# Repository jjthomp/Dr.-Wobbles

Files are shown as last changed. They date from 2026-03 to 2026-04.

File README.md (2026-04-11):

# Dr. Wobbles – Low-Cost Open Source Pain Relief Device

Dr. Wobbles is a compact, wearable medical device designed to reduce procedural pain during injections through combined vibration and cooling. It was developed by UBC SBME Capstone Team 12 in partnership with the Digital Lab (September 2025 – April 2026), with a primary focus on children living with Juvenile Idiopathic Arthritis (JIA) and broader applicability across injection-based clinical settings.

---

## Repository Contents

### 📁 `/PCB`
Contains all files required for PCB fabrication and assembly.
- Gerber files (for PCB manufacturer submission)
- Drill files
- Bill of Materials (BOM)
- Fusion Electronics source files
- PCB schematic and routing diagrams

> For assembly instructions, see the [Assembly Guide](#assembly--instructions-for-use) section below.

---

### 📁 `/CAD`
Contains all 3D model files for the mechanical housing, designed in OnShape.
- `housing_bottom.stl` – Bottom housing piece with battery and motor slots
- `housing_lid.stl` – Top lid piece with twist-and-lock mechanism and strap tabs
- `pcb_holder.stl` – Circuit board housing insert (for use with custom PCB)
- `breadboard_holder.stl` – Circuit board housing insert (for use with breadboard prototype)
- OnShape source files

> All parts are designed to be 3D printed.

---

### 📁 `/Software`
Contains the firmware for the Adafruit QTPY ESP32-S2 microcontroller.
- `dr_wobbles.ino` – Main Arduino firmware file

**Key firmware features:**
- Two vibration intensities: LOW (PWM 120/255) and HIGH (PWM 255/255)
- 5-minute auto-shutoff on HIGH setting
- Light-sleep mode during OFF state to conserve battery
- Debounce logic for button inputs

To set up the Arduino environment for the QTPY ESP32-S2, follow the official Adafruit guide:  
👉 https://learn.adafruit.com/adafruit-qt-py-esp32-s3/arduino-ide-setup-4mb-2mb-psram

### 📁 `/Docs`
Contains the complete bill of materials and sticker design
- Sticker design
- Bill of materials

> For assembly instructions, see the [Assembly Guide](#assembly--instructions-for-use) section below.
---

## Assembly & Instructions for Use

Full step-by-step assembly and usage guides are available online:

- **Assembly Manual:** https://jjthomp.github.io/Dr.-Wobbles/
- **Instructions for Use:** https://jjthomp.github.io/Dr.-Wobbles/

---

## License
This project is open source. All hardware, software, and documentation are freely available for use, modification, and distribution. Please credit UBC SBME Capstone Team 12 and the Digital Lab if you build upon this work.

---

## Contact
For questions about this project, please contact the Digital Lab or open an issue in this repository.

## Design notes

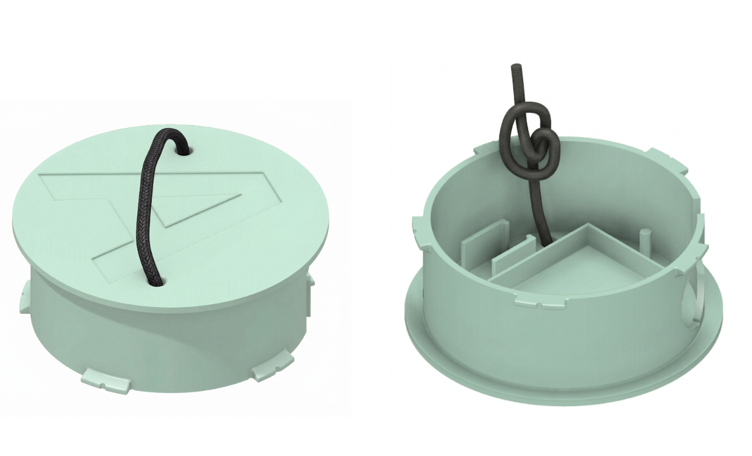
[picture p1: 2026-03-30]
images/elasticband.png

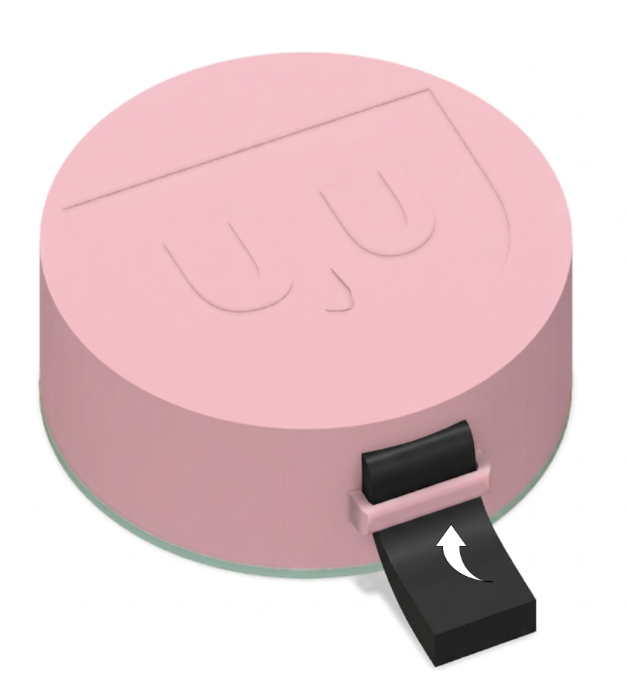
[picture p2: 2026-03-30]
images/strap.png

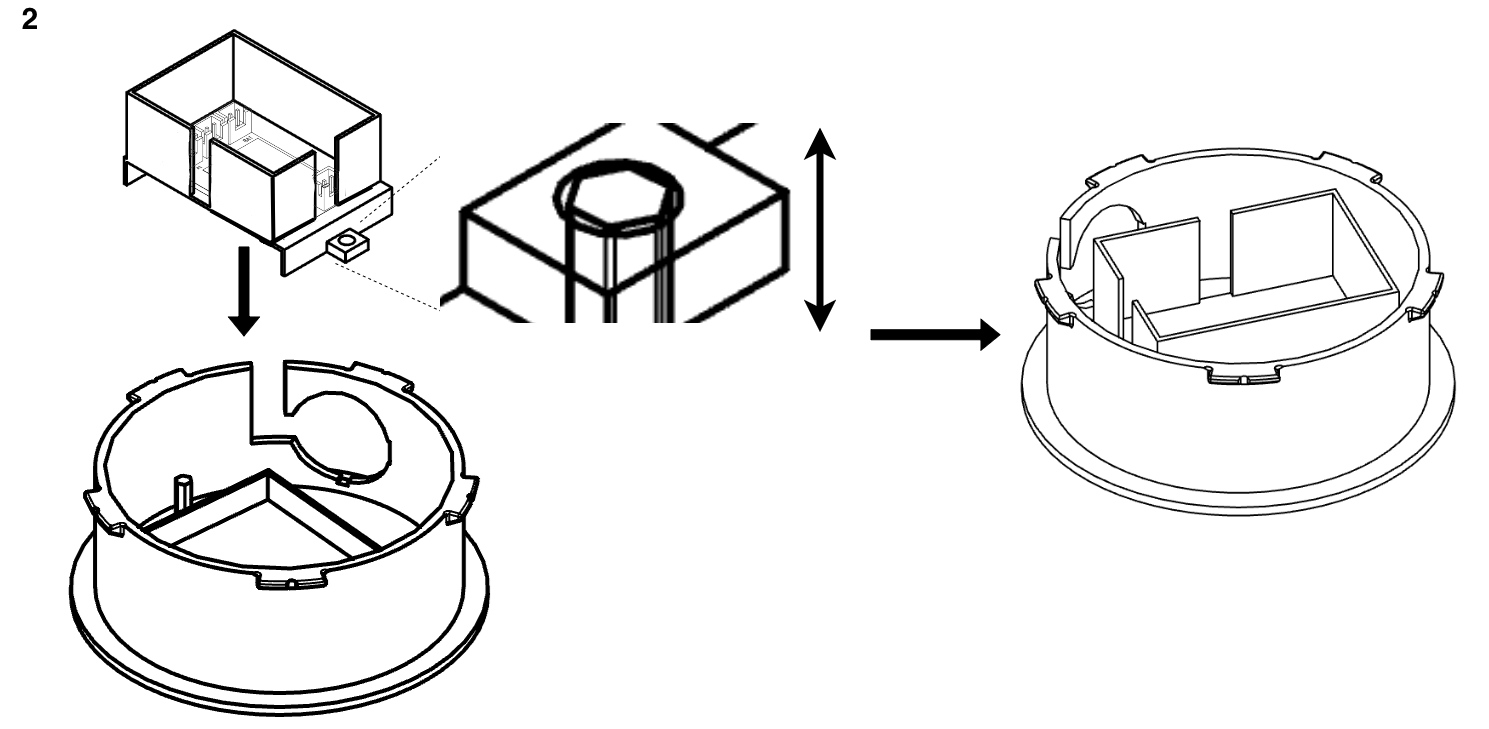
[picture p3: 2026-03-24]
images/IFU-Copy of Page-2.drawio.png

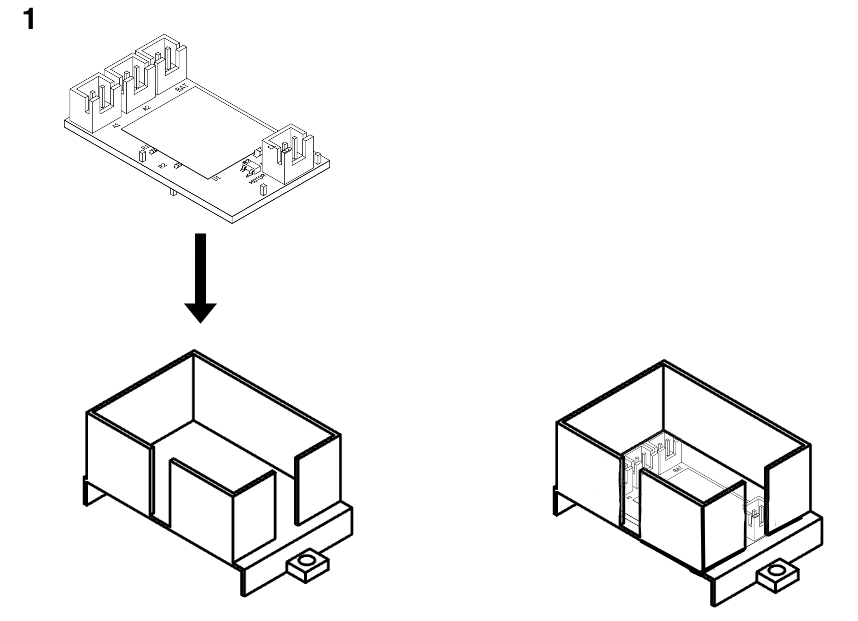
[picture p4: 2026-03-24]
images/IFU-Page-2.drawio.png

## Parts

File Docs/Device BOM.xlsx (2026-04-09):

Product | Qty | Manufacturer | Supplier/Website Name | Cost per part (CAD) | Cost total | Website Link | Notes | Total Cost
ADAFRUIT QT PY ESP32 PICO - WIFI | 1 | Adafruit Industries LLC | Digikey | 20.72 | 20.72 | https://www.digikey.ca/en/products/detail/adafruit-industries-llc/5395/21283810?gclsrc=aw.ds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 | Microcontroller | 53.78
VIBRATION MOTOR 16K RPM 6.0G | 1 | Vybronics Inc | Digikey | 4.17 | 4.17 | https://www.digikey.com/en/products/detail/vybronics-inc/VJP12-25F190/21800200 | Motor
CONN HEADER VERT 2POS 2.5MM | 2 | JST Sales America Inc. | Digikey | 0.11 | 0.22 | https://www.digikey.ca/short/3wn37qv3 | Button connectors, male
CONN HEADER VERT 2POS 2MM | 1 | JST Sales America Inc. |  | 0.14 | 0.14 | https://www.digikey.ca/short/9w7r2089 | Battery connector, male
Female 2.5 | 2 | JST Sales America Inc. | Digikey | 0.16 | 0.32 | https://www.digikey.ca/en/products/detail/jst-sales-america-inc/XHP-2/555485 | Button connectors, female
LIPOLY BATTERY CHARGER W/USB C | 1 | Adafruit | Digikey | 9.02 | 9.02 | https://www.digikey.ca/en/products/detail/adafruit-industries-llc/4410/10673110?gclsrc=aw.ds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 | Battery charger
Button | 1 | E-Switch | Digikey | 2.94 | 2.94 | http://digikey.ca/en/products/detail/e-switch/R4DBLKBLKBF0/1805285?gclsrc=aw.ds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 | Switch button
Hookup Wire | 1 | Adafruit | Digikey | 0.00 | 0 | https://www.digikey.ca/en/products/detail/adafruit-industries-llc/3175/6198258?gclsrc=aw.ds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 | Wire for connectors, negligible cost ($0.02/ft) and < 1 ft total wire required
Crimp connectors | 4 | Civilux USA | Digikey | 0.05 | 0.2 | https://www.digikey.ca/en/products/detail/cvilux-usa/CI33T021PE0/13176881?gclsrc=aw.ds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 | Crimp connectors
Ice Pack | 1 | HEQU | Amazon | 1.08 | 1.08 | https://www.amazon.ca/Reusable-Injuries-Compress-Professional-Enthusiasts/dp/B0CX1NKH7N | Ice packs
Velcro | 1 | Velcro | Michaels | 6.99 | 1.75 | https://canada.michaels.com/product/velcro-brand-onewrap-black-roll-4ft-10218638 | Estimated by length of velcro used
Elastic band | 1 | QingLHC | Amazon | 1.00 | 1 | https://www.amazon.ca/Elastic-8-Inch-10Yards-Stretch-Camping/dp/B0D7LD1LSN | Elastic for ice pack, estimated use
PCBA | 1 | JLCPCB | JLCPCB | 1.42 | 1.42 | https://jlcpcb.com/ | Gerber and drill files available on GitHub
LiPo Rechargeable Battery (Option 1) | 1 | EEMB | Amazon | 18.79 | 0 | https://www.amazon.ca/dp/B08FD39Y5R?ref=ppx_yo2ov_dt_b_fed_asin_title&th=1 | 3.7V 1000 mAh rechargeable battery used in prototype, but lower cost alternative has been found
LiPo Rechargeable Battery (Option 2) | 1 | Generic | Amazon | 10.8 | 10.8 | https://www.amazon.ca/523450-Rechargeable-Connector-Household-Appliances/dp/B0C4YH3JSV?mcid=6a1224694691310bbd7f4acc061777f4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 | 3.7V 1000 mAh rechargeable battery - lower cost

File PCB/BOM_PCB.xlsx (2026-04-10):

Comment | Designator | Footprint | JLCPCB Part #（optional）
1N4148W | D1 | SOD-123
0.1 uf | C1 | 0603
10k | R2 | 0402
310 | R1 | 0402
4.7 uf | C2 | 0603
AO3400 | U2 | SOT-23

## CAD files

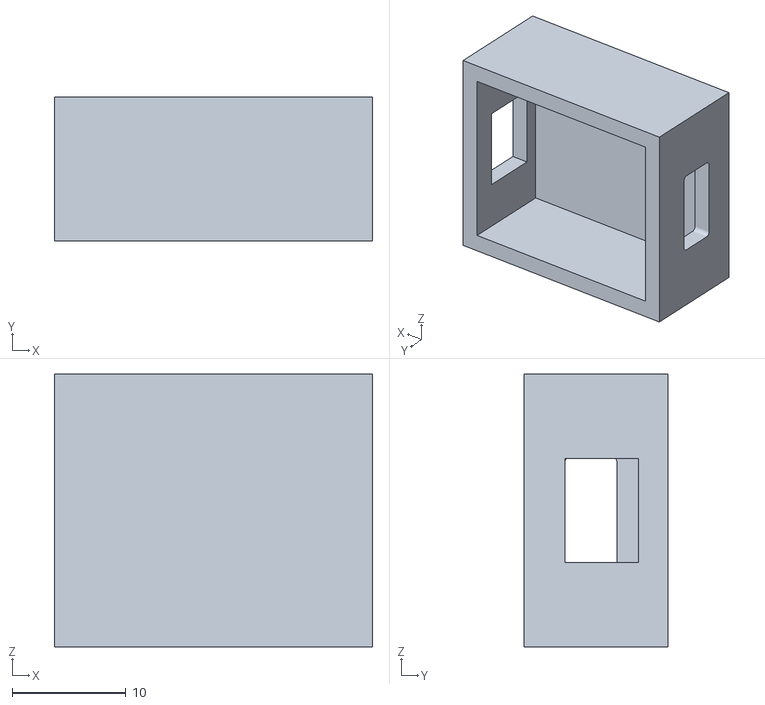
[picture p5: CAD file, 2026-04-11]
CAD/Charging base.STL
28.0 x 12.7 x 24.0

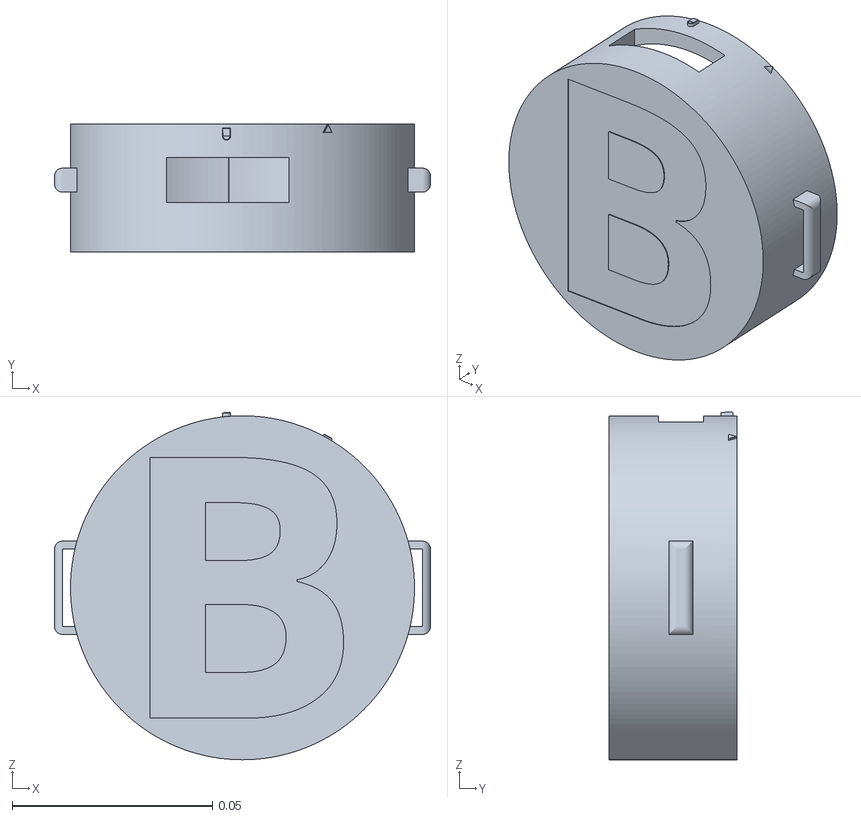
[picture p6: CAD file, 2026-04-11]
CAD/Dr. Wobbles Part B (Top).stl
0.094 x 0.032 x 0.0869

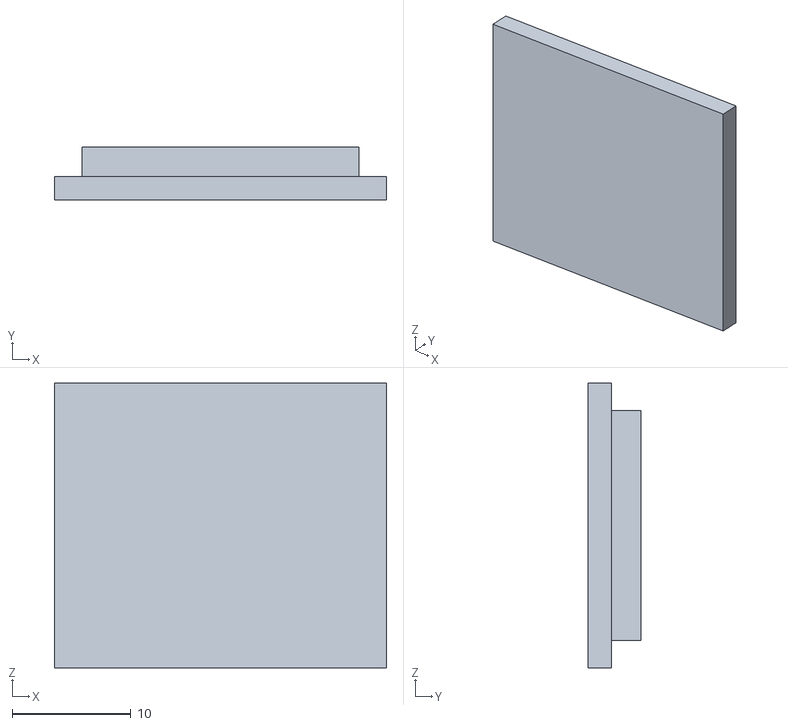
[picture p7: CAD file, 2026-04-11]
CAD/Charging lid.STL
28.0 x 4.50 x 24.0

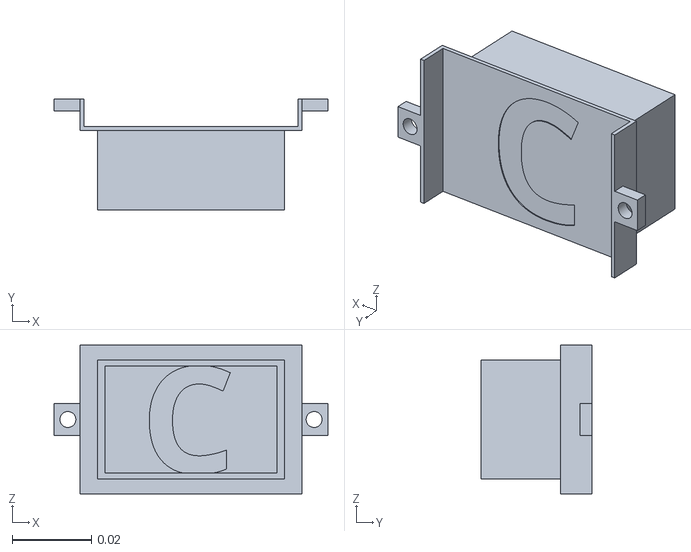
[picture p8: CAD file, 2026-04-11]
CAD/Dr. Wobbles Part C (Circuit Board Buffer).stl
0.069 x 0.028 x 0.0375

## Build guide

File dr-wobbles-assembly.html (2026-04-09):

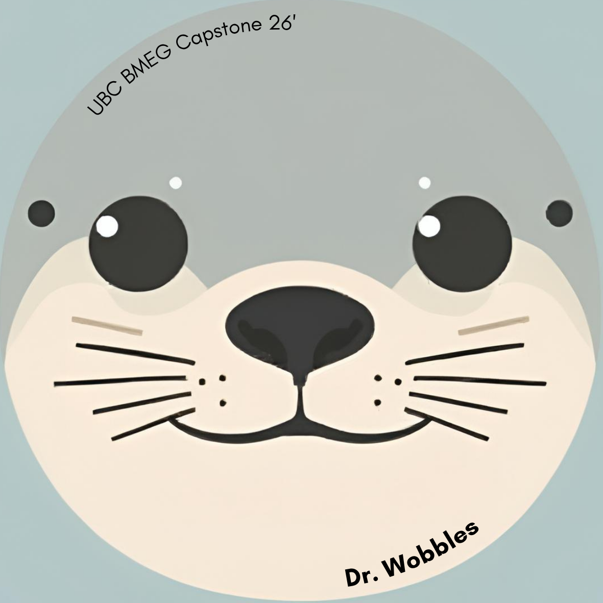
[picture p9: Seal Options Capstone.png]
Dr. Wobbles Logo


# Dr. Wobbles Assembly Instructions

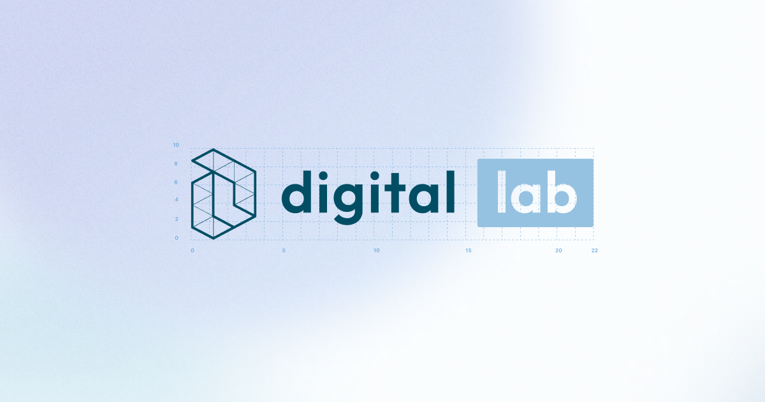
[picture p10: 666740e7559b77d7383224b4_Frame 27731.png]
Digital Lab Logo


Welcome! Select your build options below to get your custom assembly guide.

### 🛠️ Your Build Configuration

Sourcing Method:

Digital Lab Kit DIY Sourcing

Device Version:

Standard Rechargeable

## Phase 1: Parts & Sourcing

You will receive all parts pre-packaged from the Digital Lab — no sourcing required.

- Request your complete kit here: [Insert Digital Lab Link]

You are sourcing all parts yourself. Here is what you need:

- Circuit Board: Order the circuit board and electrical components using our files here: [Insert Circuit Board File Link]
- All Other Parts: Order everything else using our Parts List: [Insert Parts List Link]

### Connector Preparation

1. Cut your wires to the correct lengths.
2. Strip a small section of insulation from each wire end.
3. Crimp a connector pin onto each stripped wire end.
4. Press the pins into the plastic connector housing until they click.
5. Solder the other ends to the motor and button, as shown in Phase 3.

## Phase 2: Printer Set-up

We have optimized these files for easy printing.

- Infill: 10% – 20%
- Supports: Required
- Orientation: Place flat on the printer bed.
- Ready-to-print files: GCODE files for common printers are available here: [Insert Sliced Files Link]

Files: Download the Standard Enclosure print files here: [Insert Standard STL Link]

Files: Download the Rechargeable Enclosure print files here: [Insert Rechargeable STL Link]

## Phase 3: Code & Connections

### 1. Loading the Software

Download all files from our GitHub: [Insert GitHub Link]. Before loading the software, set up the Arduino environment and add the microcontroller by following this guide: Arduino IDE Setup Guide (https://learn.adafruit.com/adafruit-qt-py-esp32-s3/arduino-ide-setup-4mb-2mb-psram). Then load the software onto the microcontroller before assembling the device.

### 2. Connecting Components

Plug each component into the correct port on the microcontroller:

- Motor: Plug into [Port X]
- Button: Plug into [Port Y]
- Battery: Plug into [Port Z]

## Phase 4: Final Assembly

Follow these steps in order. Refer to the images for exact placement.

### 1. Materials Overview

Lay out all your parts before starting: the two printed enclosure halves, circuit board, battery, motor, elastic bands, straps, and sticker.

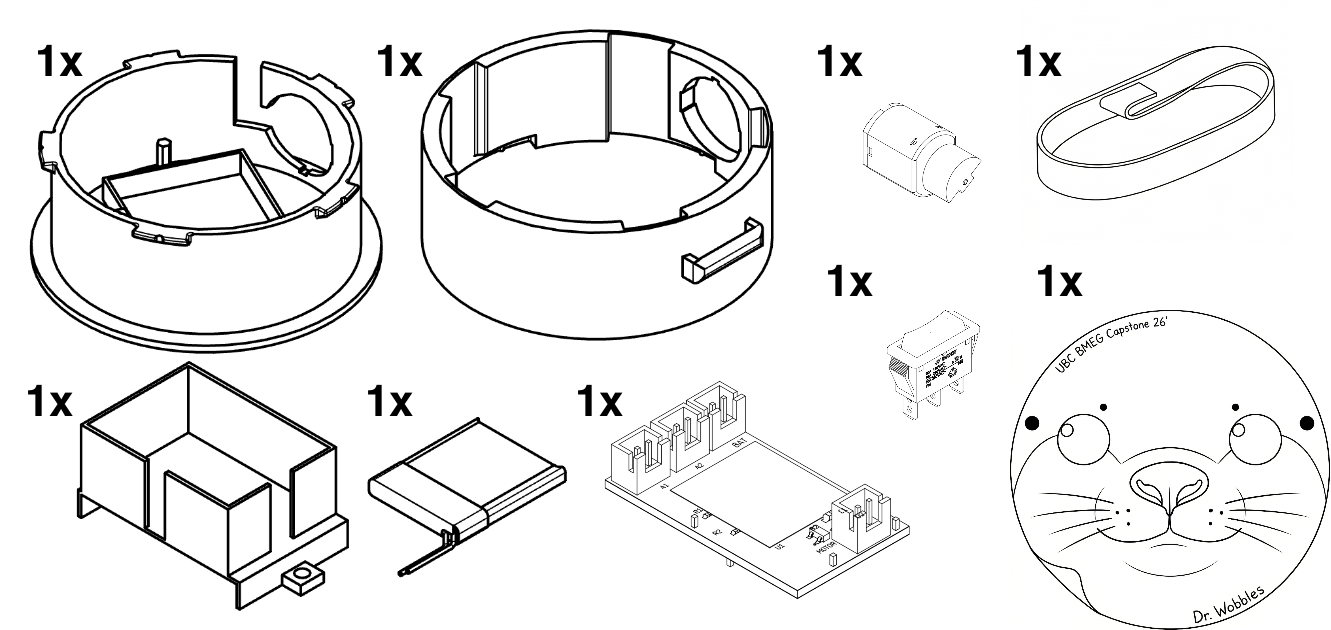
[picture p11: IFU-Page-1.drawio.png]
All parts laid out


### 2. Elastic Band Placement

Thread the elastic bands through the two slots on the back of the enclosure. Tie a knot on each end to hold them in place.

Placing the elastic bands

### 3. Battery Insertion

Place the battery into the lower compartment of the enclosure.

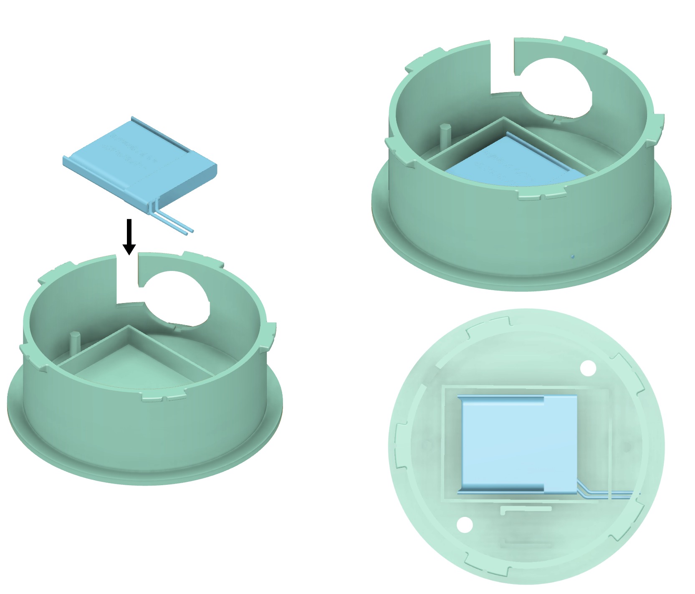
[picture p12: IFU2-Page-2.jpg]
Battery placed in enclosure


### 4. Motor Placement

Press the motor into its slot until it sits flat. Apply a small dot of hot glue or super glue around the base to hold it in place.

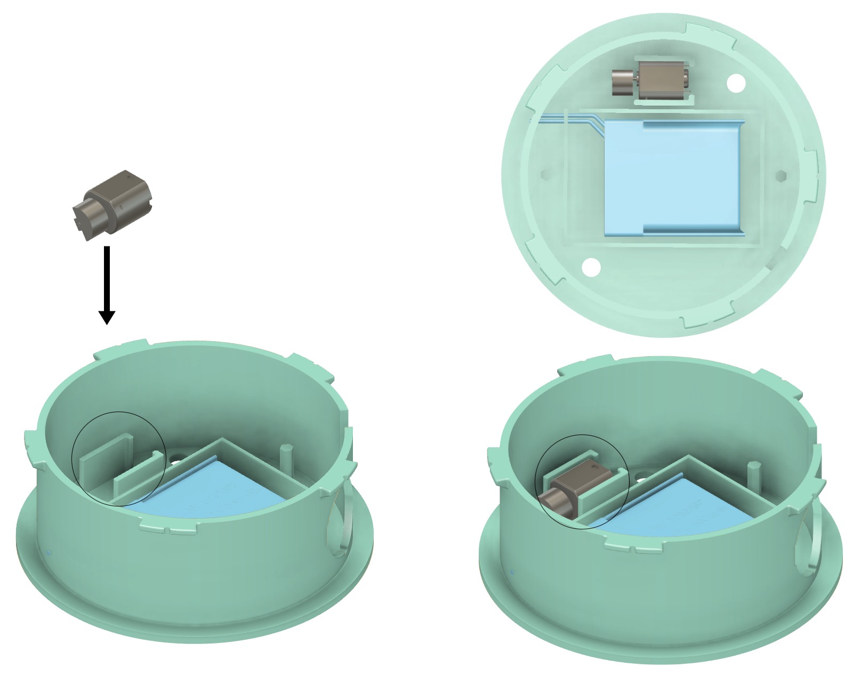
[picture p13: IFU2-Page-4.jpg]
Motor seated in slot


### 5. Circuit Board Placement

Slide the circuit board into the slot above the battery. Apply a small dot of hot glue or super glue to hold it in place.

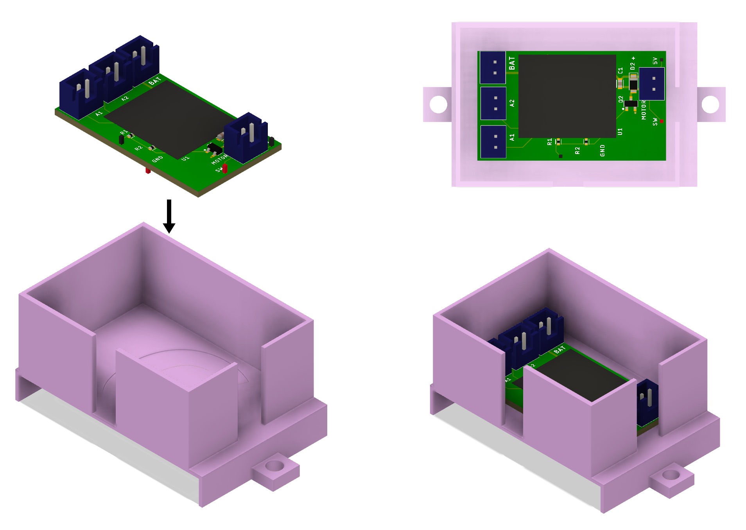
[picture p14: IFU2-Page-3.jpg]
Circuit board placed in enclosure


### 6. Circuit Board Holder

Press the printed holder down over the circuit board to keep it in place.

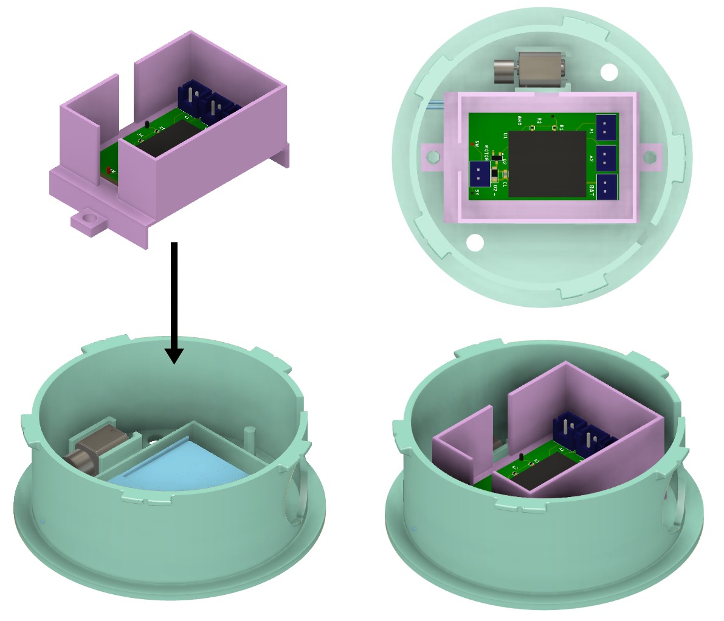
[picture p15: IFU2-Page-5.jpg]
Circuit board holder pressed into place


### 7. Wire Connections

Plug each connector into its matching port on the circuit board. Make sure each connector clicks in fully.

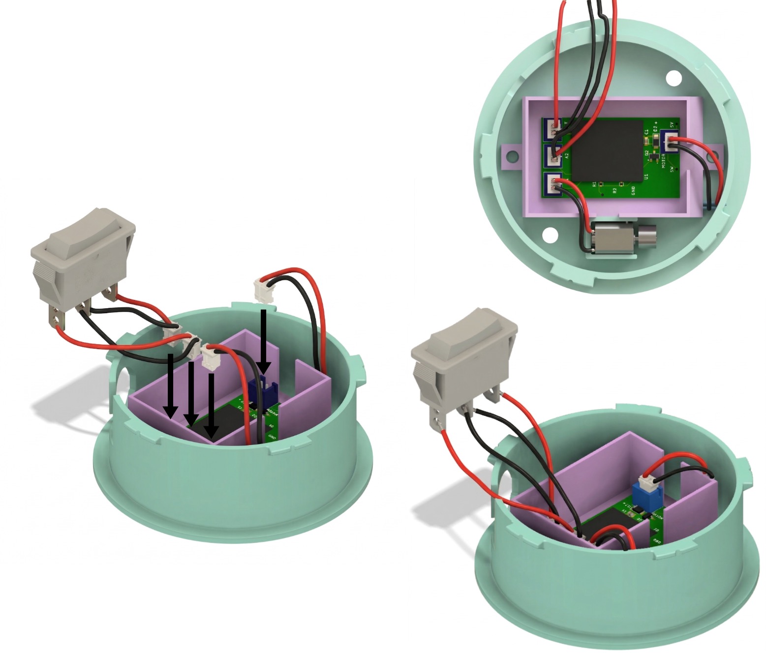
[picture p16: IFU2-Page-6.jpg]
Wire connection step


### 8. Close the Enclosure

Line up the two halves of the enclosure and press them together. Check that no wires are caught in the seam. Twist to lock.

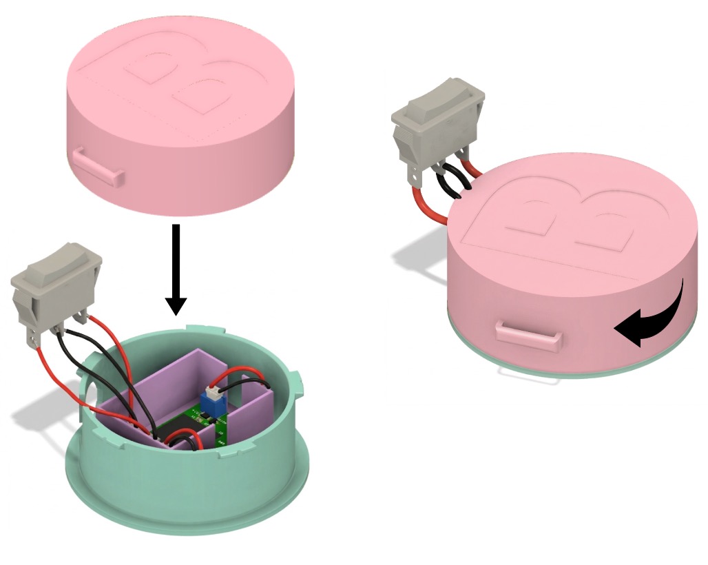
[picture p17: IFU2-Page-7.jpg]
Closing the device halves


### 9. Strap Insertion

Thread each strap through the side loops, fold the end over, and sew it down.

Inserting the fabric straps

### 10. Sticker Placement

Peel and apply the seal sticker to the front of the device.

Applying the final front sticker

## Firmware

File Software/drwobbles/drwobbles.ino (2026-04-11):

// Pin assignments
const int motorPin  = A1;  // DAC-capable true analog output
const int leftPin   = A2;  // Switch left position (LOW_SPEED)
const int rightPin  = A3;  // Switch right position (HIGH_SPEED)

// Motor settings
const int LOW_INTENSITY      = 120;
const int HIGH_INTENSITY     = 255;
const int KICKSTART_DURATION = 100;
const int DEBOUNCE_DELAY     = 200;

// State
enum MotorState { MOTOR_OFF, LOW_SPEED, HIGH_SPEED };
MotorState currentState = MOTOR_OFF;

bool lastLeftState  = HIGH;
bool lastRightState = HIGH;

void kickstart() {
  analogWrite(motorPin, 255);
  Serial.println("Kickstarting motor...");
  delay(KICKSTART_DURATION);
}

void applyMotorState() {
  switch (currentState) {
    case MOTOR_OFF:
      analogWrite(motorPin, 0);
      Serial.println("Motor: OFF");
      break;
    case LOW_SPEED:
      kickstart();
      analogWrite(motorPin, LOW_INTENSITY);
      Serial.println("Motor: LOW");
      break;
    case HIGH_SPEED:
      kickstart();
      analogWrite(motorPin, HIGH_INTENSITY);
      Serial.println("Motor: HIGH");
      break;
  }
}

void setup() {
  Serial.begin(115200);
  pinMode(motorPin,  OUTPUT);
  pinMode(leftPin,   INPUT_PULLUP);  // Switch COM → GND
  pinMode(rightPin,  INPUT_PULLUP);  // Switch COM → GND
  analogWrite(motorPin, 0);
  Serial.println("Setup done!");
}

void loop() {
  bool leftRead  = digitalRead(leftPin);
  bool rightRead = digitalRead(rightPin);

  // Temporary debug — add this
  Serial.print("Left: "); Serial.print(leftRead);
  Serial.print(" | Right: "); Serial.println(rightRead);
  delay(100);
  
  // ... rest of your loop
  // Middle position — both HIGH (floating with pullup) → OFF
  if (leftRead == HIGH && rightRead == HIGH) {
    if (currentState != MOTOR_OFF) {
      currentState = MOTOR_OFF;
      applyMotorState();
    }
  }

  // Left pressed → LOW_SPEED
  if (lastLeftState == HIGH && leftRead == LOW) {
    currentState = LOW_SPEED;
    applyMotorState();
    delay(DEBOUNCE_DELAY);
  }

  // Right pressed → HIGH_SPEED
  if (lastRightState == HIGH && rightRead == LOW) {
    currentState = HIGH_SPEED;
    applyMotorState();
    delay(DEBOUNCE_DELAY);
  }

  lastLeftState  = leftRead;
  lastRightState = rightRead;
}

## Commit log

2026-03-30 PCB Files
2026-03-30 BOM for PCB manufacturer
    [BOM_PCB.xlsx]
2026-04-09 Rename Screenshot 2026-03-25 at 11.28.23 PM.png to elasticband.png
2026-04-09 Rename Screenshot 2026-03-25 at 11.15.29 PM.png to strap.png
2026-04-09 Update connector preparation and enclosure closing steps
2026-04-10 Dr Wobbles Schematic
    [Seal.sch]
2026-04-11 merged with main
    [Charging base.STL, Charging lid.STL, Dr. Wobbles Part B (Top).stl, Dr. Wobbles Part C (Circuit Board Buffer).stl]
2026-04-11 Rename Charging base.STL to CAD/Charging base.STL
    [Charging base.STL]
2026-04-11 Rename Charging lid.STL to CAD/Charging lid.STL
    [Charging lid.STL]
2026-04-11 Rename Device BOM.xlsx to Docs/Device BOM.xlsx
    [Device BOM.xlsx]
2026-04-11 Rename Dr. Wobbles Part B (Top).stl to CAD/Dr. Wobbles Part B (Top).stl
    [Dr. Wobbles Part B (Top).stl]
2026-04-11 Rename Dr. Wobbles Part C (Circuit Board Buffer).stl to CAD/Dr. Wobbles Part C (Circuit Board Buffer).stl
    [Dr. Wobbles Part C (Circuit Board Buffer).stl]
2026-04-11 Rename Dr.Wobbles - Part A Bottom.stl to CAD/Dr.Wobbles - Part A Bottom.stl
    [Dr.Wobbles - Part A Bottom.stl]
2026-04-11 Update file paths for PCB and CAD resources
